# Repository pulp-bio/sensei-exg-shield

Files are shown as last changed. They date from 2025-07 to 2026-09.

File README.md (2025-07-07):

# SENSEI ExG shield

This repository contains the hardware design files for the **SENSEI ExG shield**, a versatile biopotential sensing shield for biopotential monitoring.

## Overview

The **SENSEI ExG Shield** provides a modular and configurable approach to biopotential measurements. It supports both balanced and unbalanced supply voltage configurations through different soldering options.

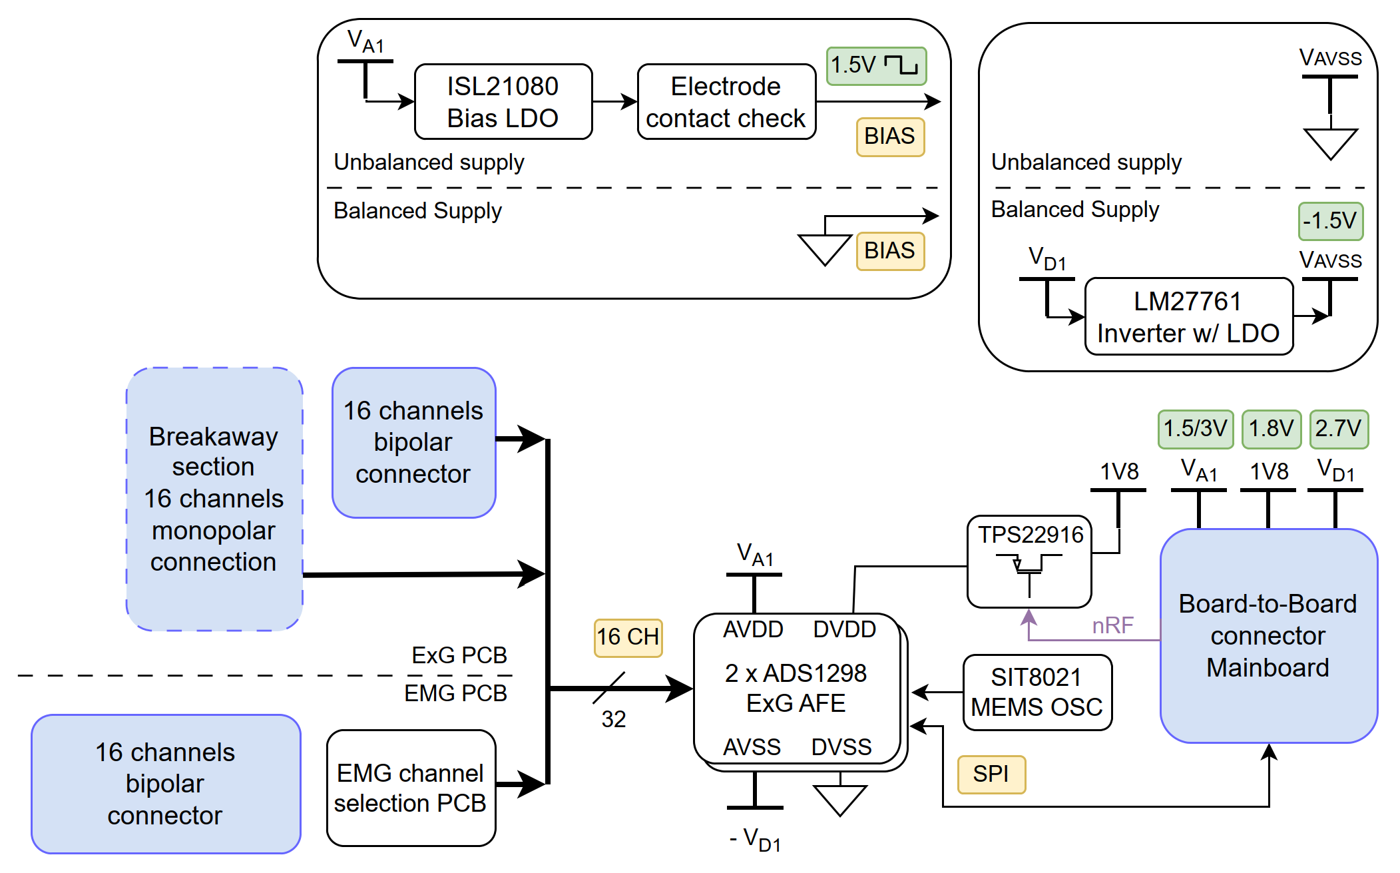
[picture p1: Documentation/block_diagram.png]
Block Diagram


### Key Features
- **16 biopotential channels**
- Supports both active and passive electrodes
- Configurable for fully differential and common-reference electrode setups
- Flexible supply voltage configuration (balanced and unbalanced)
- Stable MEMS-based clock (±50 ppm accuracy)

## Changelog
A changelog is available in the [Changelog.md](Changelog.md) file, which tracks all major updates and revisions to the board's design and documentation.

## Contributors
- **Sebastian Frey** ([sefrey@iis.ee.ethz.ch](mailto:sefrey@iis.ee.ethz.ch))

## License
This repository makes use of the following licenses:
- for all *hardware*: Solderpad Hardware License Version 0.51
- for all *images*: Creative Commons Attribution 4.0 International
License][cc-by]

For further information have a look at the license files: `LICENSE.hw`, `LICENSE.images`

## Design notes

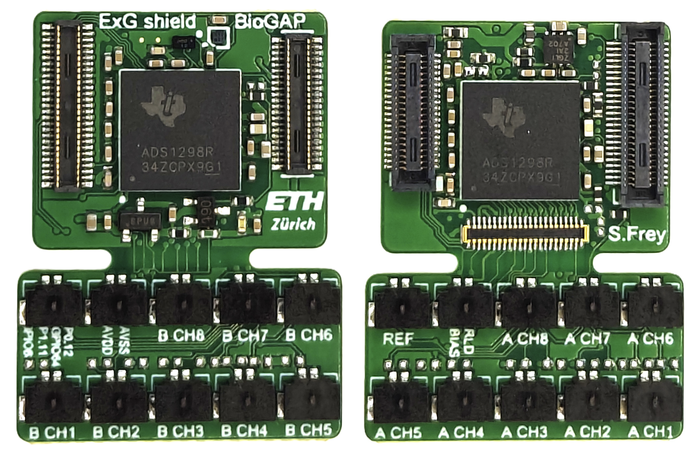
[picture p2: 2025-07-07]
Documentation/image_pcb.png

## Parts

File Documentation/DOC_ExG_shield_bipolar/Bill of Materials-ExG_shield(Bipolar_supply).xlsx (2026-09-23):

Comment | Description | Designator | Footprint | LibRef | Quantity
CL05A104KA5NNNC | Cap Ceramic 100nF 25V X5R ±10% SMD 0402 +85°C Paper T/R | C1, C3, C4, C7, C10, C15, C17, C18, C22, C25, C32, C33, C34, C40, C41, C43 | FP-CL278-IPC_C | CMP-13271-000728-1 | 16
CL05A105KP5NNNC | Cap Ceramic 1uF 10V X5R ±10% SMD 0402 +85°C Paper T/R | C2, C5, C6, C9, C11, C12, C16, C19, C20, C24, C26, C27, C37, C39, C42 | FP-CL511-IPC_C | CMP-13271-001936-1 | 15
CL05A106MP8NUB8 | Cap Ceramic 10uF 10V X5R ±20% SMD 0402 +85°C Paper T/R | C8, C23, C31 | FP-CL07-IPC_C | CMP-13271-002778-1 | 3
04025C102KAT2A | General Purpose Ceramic Capacitor, 0402, 1nF, 10%, X7R, 15%, 50V | C13, C28 | FP-0402-L_1_0_1-W_0_5_0_1-IPC_B | CMP-2008-02699-2 | 2
CL05A226MQ5QUNC | Cap Ceramic 22uF 6.3V X5R ±20% SMD 0402 +85°C Paper T/R | C14, C29 | FP-CL746-IPC_C | CMP-13271-000286-1 | 2
GRM155R71H152KA01D |  | C21 | CAPC1005X55X25NL05T10 | CMP-2008-04642-1 | 1
CGA2B3X7R1V103K050BB | Cap Ceramic 10nF 35V X7R 10% Pad SMD 0402 +125°C Automotive T/R | C30 | FP-CGA2B-MFG | CMP-08246-000497-1 | 1
GRM155Z71A225KE01D | Chip Multilayer Ceramic Capacitors for General Purpose, 0402, 2.2uF, X7R, 15%, 10%, 10V | C35 | FP-GRM155-0_15-IPC_B | CMP-06035-048202-1 | 1
CL05A475MP5NRNC | Cap Ceramic 4.7uF 10V X5R ±20% SMD 0402 +85°C Paper T/R | C36, C38 | FP-CL282-IPC_C | CMP-13271-000548-1 | 2
DF52-2S-0.8H_21_ | Connector | J1, J2, J7, J8, J9, J10, J11, J12, J13, J14, J15, J16, J17, J18, J19, J20, J21, J22, J23, J25 | DF522S08H21 | DF52-2S-0.8H_21_ | 20
DF40HC(2.5)-40DS-0.4V(51) | 40 Position 0.4mm Pitch Dual Row Vertical Surface Mount (SMT) Pin Socket, 2.5mm Stacking Height | J3 | DF40HC3040DS04V51 | DF40HC(3.0)-40DS-0.4V(51) | 1
DF40HC(2.5)-50DS-0.4V(51) | 50 Position 0.4mm Pitch Dual Row Vertical Surface Mount (SMT) Pin Socket, 2.5mm Stacking Height | J4 | DF40HC3050DS04V51 | DF40HC(3.0)-50DS-0.4V(51) | 1
DF40C-40DP-0.4V(51) | 50 Position 0.4mm Pitch Dual Row Vertical Surface Mount (SMT) Receptacle | J5 | FP-DF40C-40DP-0_4V_51-MFG | DF40C-40DP-0.4V(51) | 1
DF40C-50DP-0.4V(51) | 50 Position 0.4mm Pitch Dual Row Vertical Surface Mount (SMT) Receptacle, | J6 | CONN_COMBI_50P | DF40C-50DP-0.4V(51) | 1
505070-4222 | Connector | J24 | 5050704222 | 505070-4222 | 1
PMSS3906 | PNP Switching Transistor | Q1 | SOT323_N | PMSS3906 | 1
MCS04020C1004FE000 | RES SMD 1M OHM 1% 1/10W 0402 | R1 | FP-MCS0402-IPC_C | CMP-02407-000443-1 | 1
RT0402BRD0745K3L | RES 45.3K OHM 1/16W .1% SMD 0402 | R2 | FP-RT0402-MFG | CMP-03412-018483-1 | 1
RN73R1ETTP2003B25 | 200kΩ ±0.1% 0.063W, 1/16W Chip Resistor 0402 (1005 Metric) Moisture Resistant Thin Film | R3 | FP-RN73R1E-IPC_C | CMP-04015-050624-1 | 1
RC0402FR-070RL | RES SMD 0 OHM JUMPER 1/16W 0402 | R4, R13, R14 | FP-RC0402-0_4-IPC_A | CMP-2002-07342-2 | 3
RT0402FRE074K7L | RES 4.70K OHM 1/16W 1% SMD 0402 | R5 | FP-RT0402-MFG | CMP-2002-02901-2 | 1
TNPW040214K2BEED | RES 14.2K OHM 1/16W 1% SMD 0402 | R6 | FP-RT0402-MFG | CMP-2002-02901-2 | 1
RT0402BRD076K34L | RES 6.34K OHM 1/16W 1% SMD 0402 | R7 | FP-RT0402-MFG | CMP-2002-02901-2 | 1
RR0510P-563-D | 56kΩ ±0.5% 0.0625W 1/16W Chip Resistor 0402 (1005 Metric) Thin Film | R8 | FP-RR0510-MFG | CMP-2002-01632-2 | 1
RC0402FR-070RL | RES SMD 0 OHM JUMPER 1/16W 0402 | R10, R11, R12, R33 | FP-RC0402-0_4-IPC_C | CMP-2002-07342-2 | 4
ADS1298RIZXGT | 8-Channel, 24-Bit ADC with Integrated Respiration Impedance and ECG Front End, -40 to 85 degC, 64-pin BGA (ZXG64), Green (RoHS & no Sb/Br) | U1, U2 | TI-ZXG64 | CMP-0003-00996-1 | 2
ISL21080CIH320Z-TK | IC VREF SERIES 0.3% SOT23-3 | U3 | FP-P3_064A-IPC_C | CMP-13559-000004-1 | 1
LM27761DSGT | IC REG CHARGE PUMP ADJ 8WSON | U4 | FP-DSG0008A-MFG | CMP-04918-000089-1 | 1
SN74AUP2G125YZPR | Low-Power Dual Bus Buffer Gate With 3-State Outputs, YZP0008ADAD, LARGE T&R | U5 | YZP0008ADAD | CMP-0859-01143-3 | 1
TPS22916CYFPR | Integrated Circuit | U6 | BGA4C40P2X2_78X78X50 | TPS22916CYFPR | 1
SIT8021AC-J3-18S-2.048000 | MEMS OSC 2.048MHZ LVCMOS | Y1 | FP-SiT8021-MFG | CMP-25159-259502-1 | 1

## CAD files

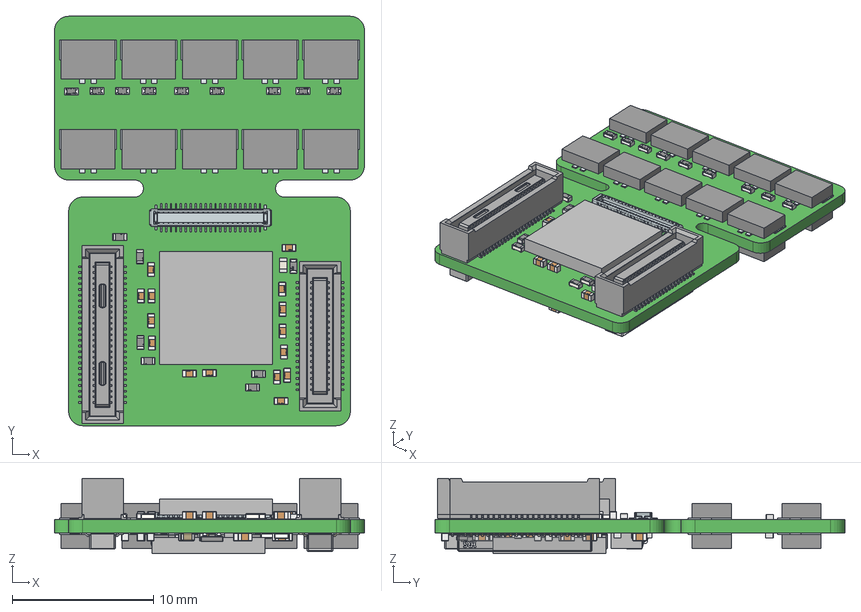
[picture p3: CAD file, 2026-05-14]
Documentation/ExG_shield_3D_step.step
21.9 x 29.0 x 5.32 mm
Pins x 20
logo x 56
pins x 20
terminals x 36
Yageo Logo x 7
Extruded x 6
Balls
0.1mm
Si Time Logo
IC_BODY
IC_LEG x 3
Renesas Logo
circle
Susumu Logo adjustable
top
TDK Logo
DF40C-50DP_RGB8421504
Hirose Electric
DF40HC(3.0)-40DS-0.4V
DF40HC(3.0)-50DS

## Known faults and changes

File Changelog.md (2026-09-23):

# Changelog

## [1.0.2] (23.09.2026)

### Added

- SPI clk of ADS A and ADS B are now disconnected when their respective CS is not low. This is done with MUX U5 (SN74AUP2G125YZPR).

### Fixed

- Unintended clear of the data ready signal of ADS A and B fixed by clk disconnection.

## [1.0.1] (14.05.2026)

### Added

### Changed

- Clock source of ADS1298 is fixed to external oscillator
- Pin from board-to-board connector nRF_P0.05 is not used anymore for clk source selection

## [1.0.0] (03.07.2025)
- Inital version

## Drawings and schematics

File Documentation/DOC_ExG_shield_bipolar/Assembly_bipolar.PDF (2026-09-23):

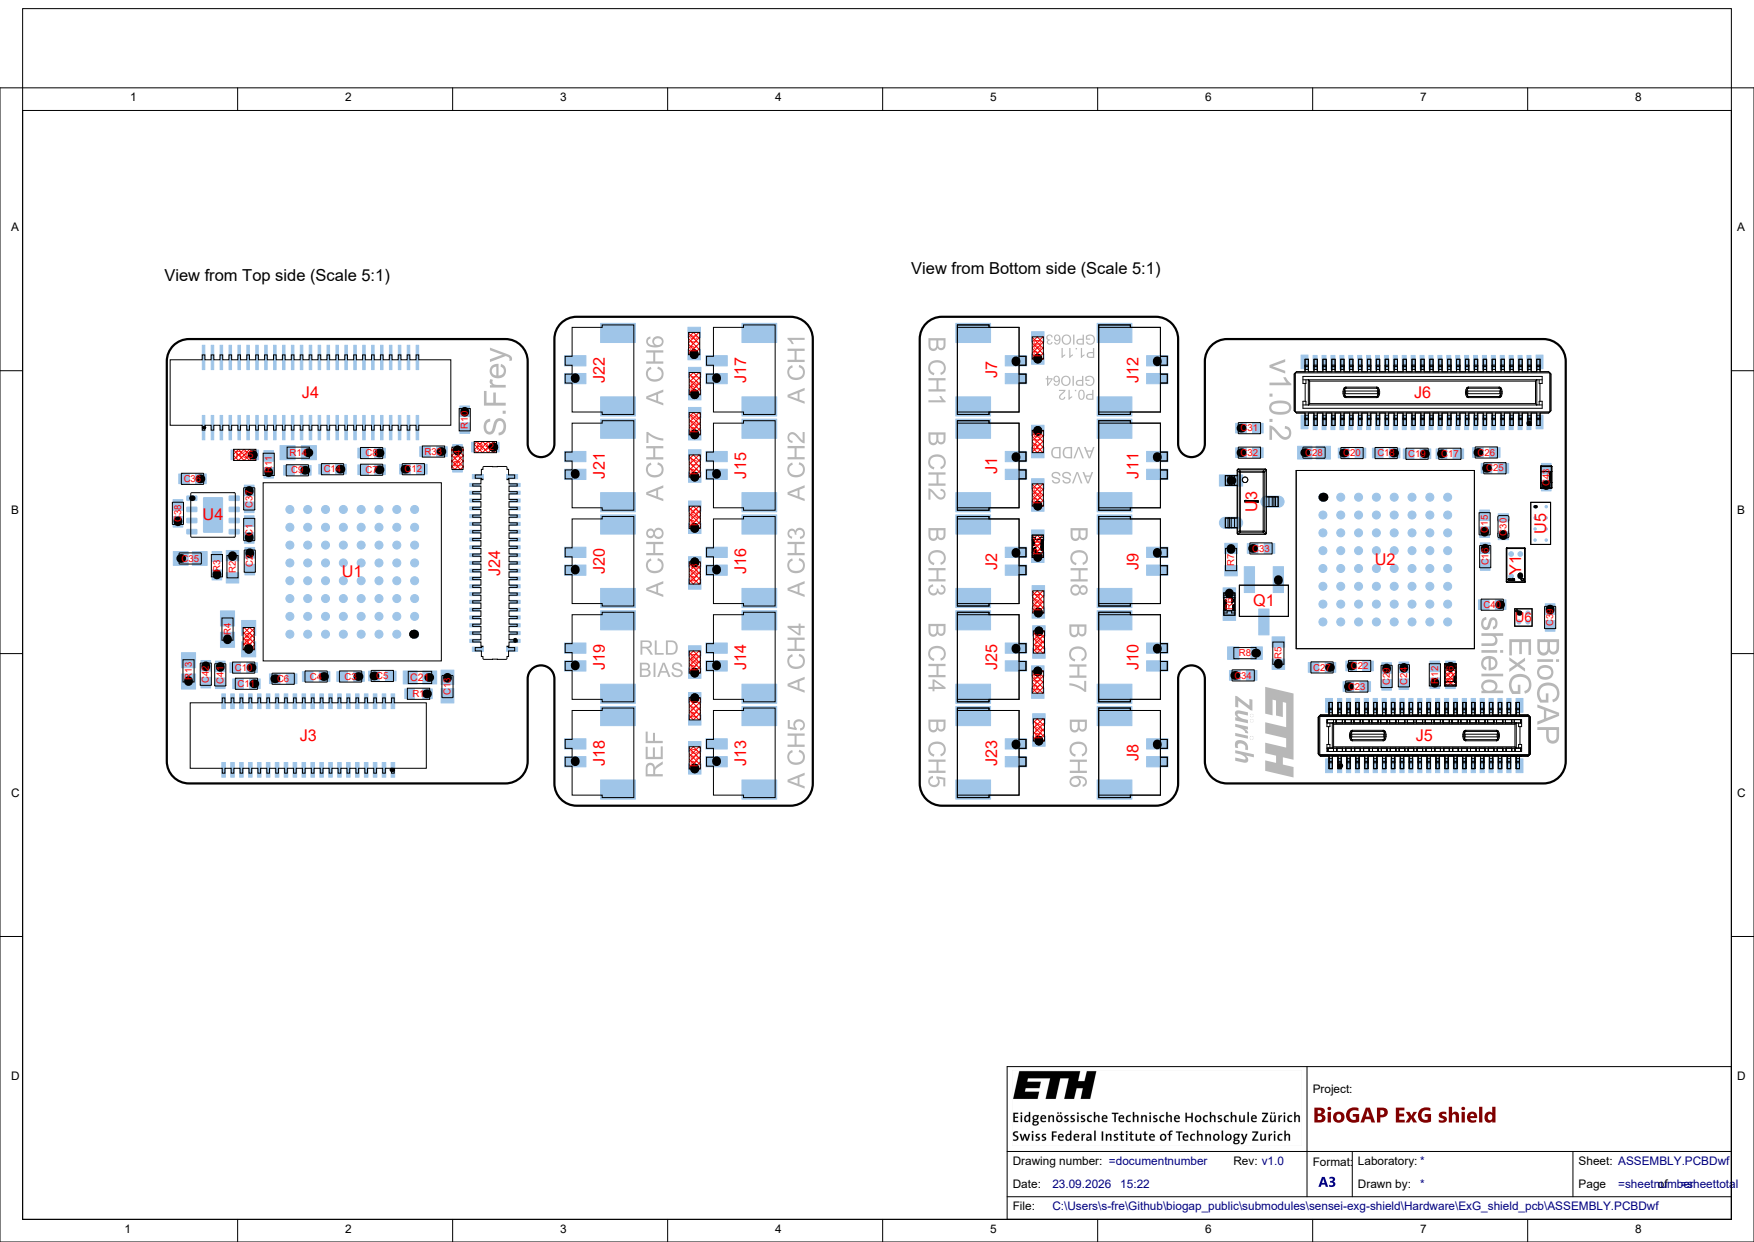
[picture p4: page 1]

View from Top side (Scale 5:1)

View from Bottom side (Scale 5:1)

Sheet:
Page =sheetnumber of =sheettotal

C:\Users\s-fre\Github\biogap_public\submodules\sensei-exg-shield\Hardware\ExG_shield_pcb\ASSEMBLY.PCBDwf

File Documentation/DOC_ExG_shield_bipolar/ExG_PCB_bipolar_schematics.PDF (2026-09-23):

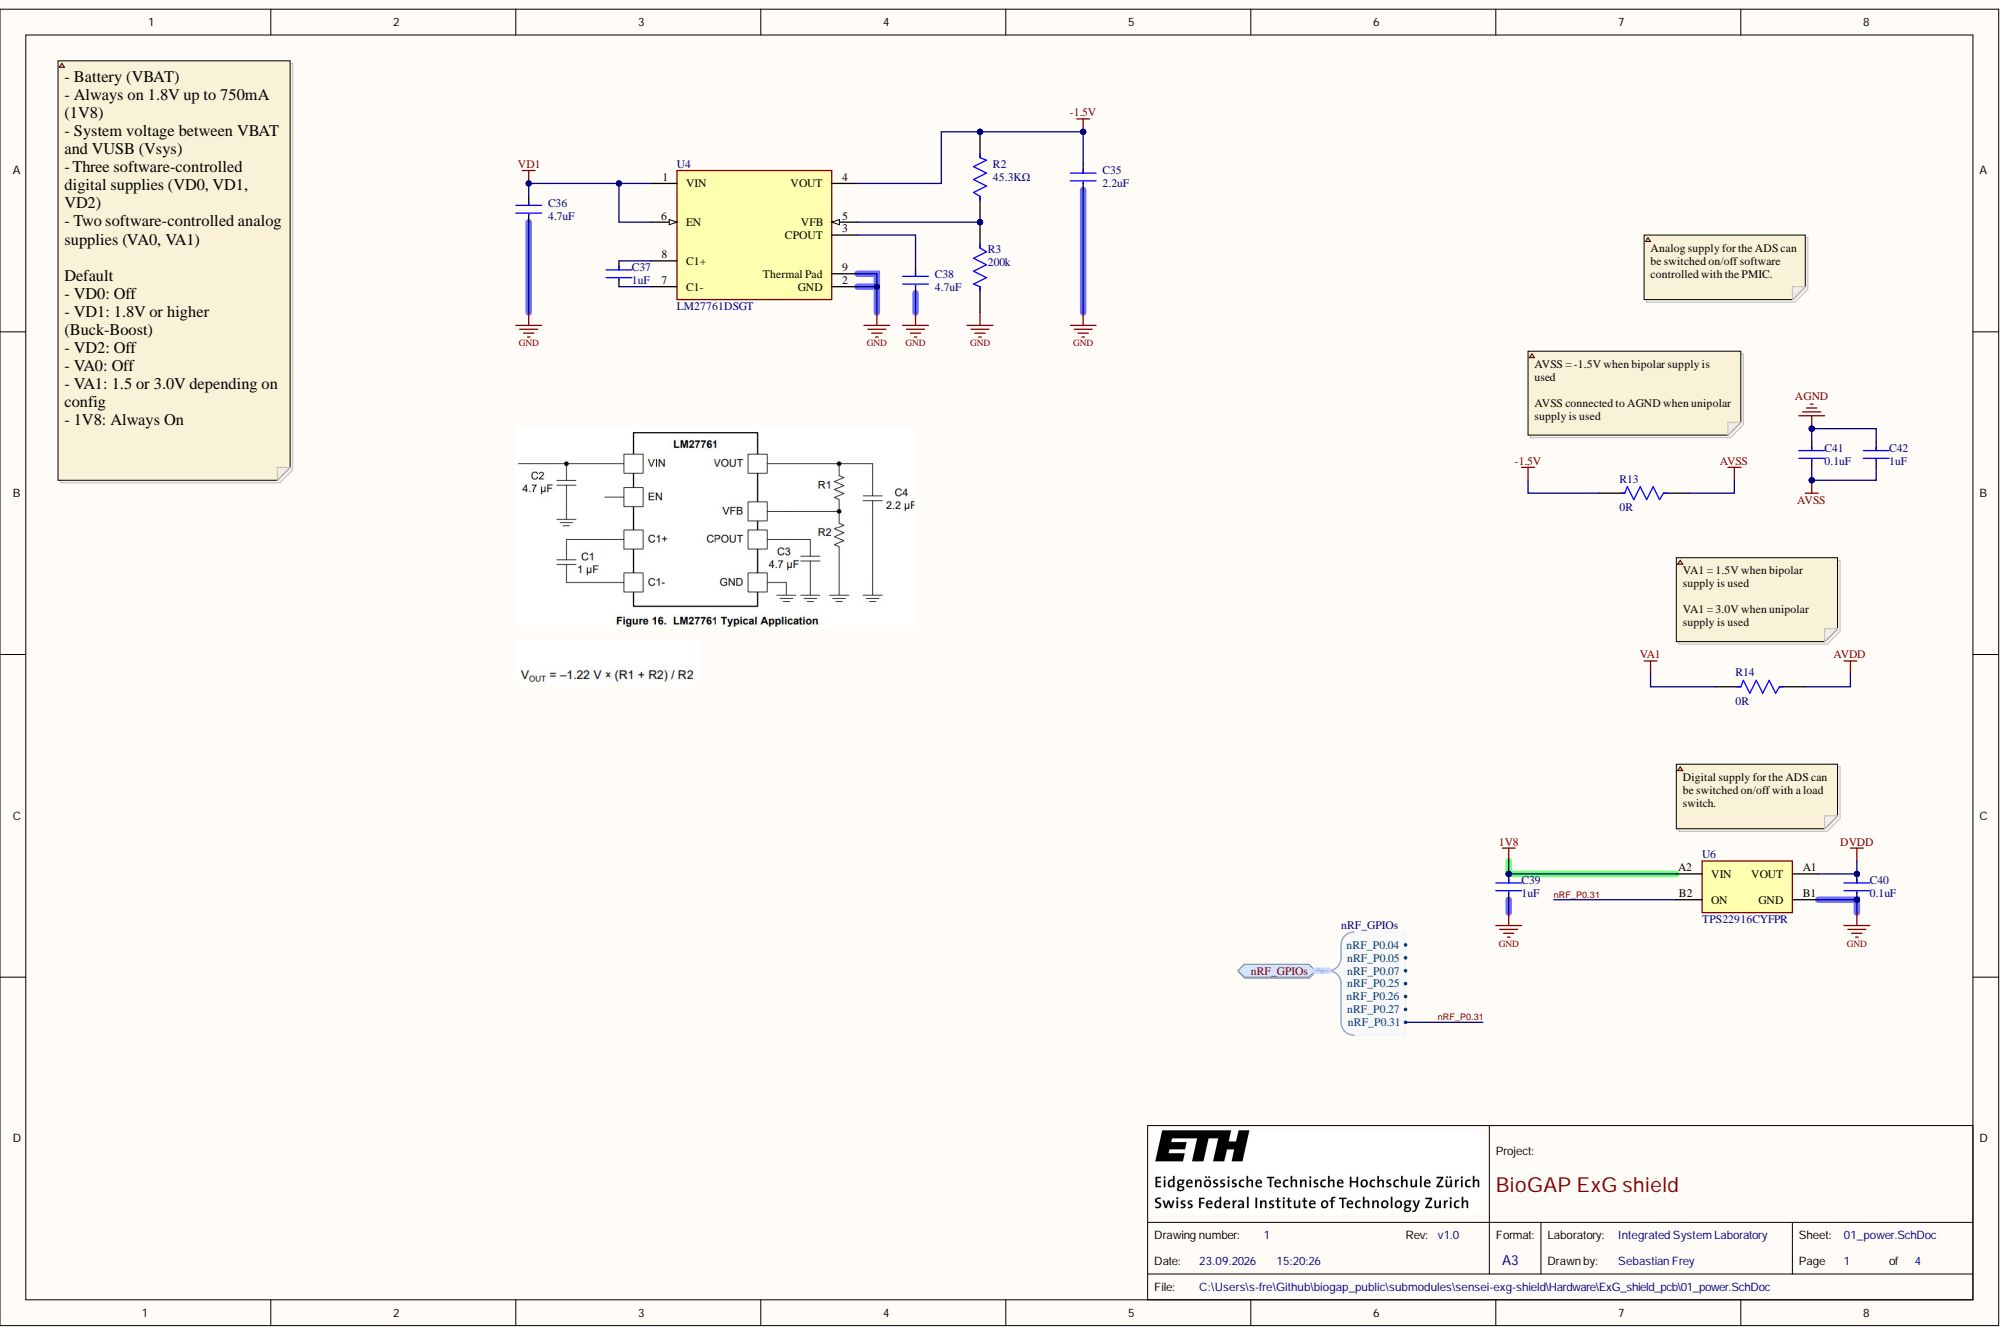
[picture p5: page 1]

- Battery (VBAT)
- Always on 1.8V up to 750mA
- System voltage between VBAT
and VUSB (Vsys)
- Three software-controlled
digital supplies (VD0, VD1,
- Two software-controlled analog
supplies (VA0, VA1)

Analog supply for the ADS can
be switched on/off software
controlled with the PMIC.

AVSS = -1.5V when bipolar supply is
used

AVSS connected to AGND when unipolar
supply is used

Digital supply for the ADS can
be switched on/off with a load
switch.

Project: BioGAP ExG shield

Drawing number: 1 Rev: v1.0 Date: 23.09.2026 15:20:26 | Format: A3 | Laboratory: Integrated System Laboratory Drawn by: Sebastian Frey | Sheet: 01_power.SchDoc Page 1 of 4

C:\Users\s-fre\Github\biogap_public\submodules\sensei-exg-shield\Hardware\ExG_shield_pcb\01_power.SchDoc

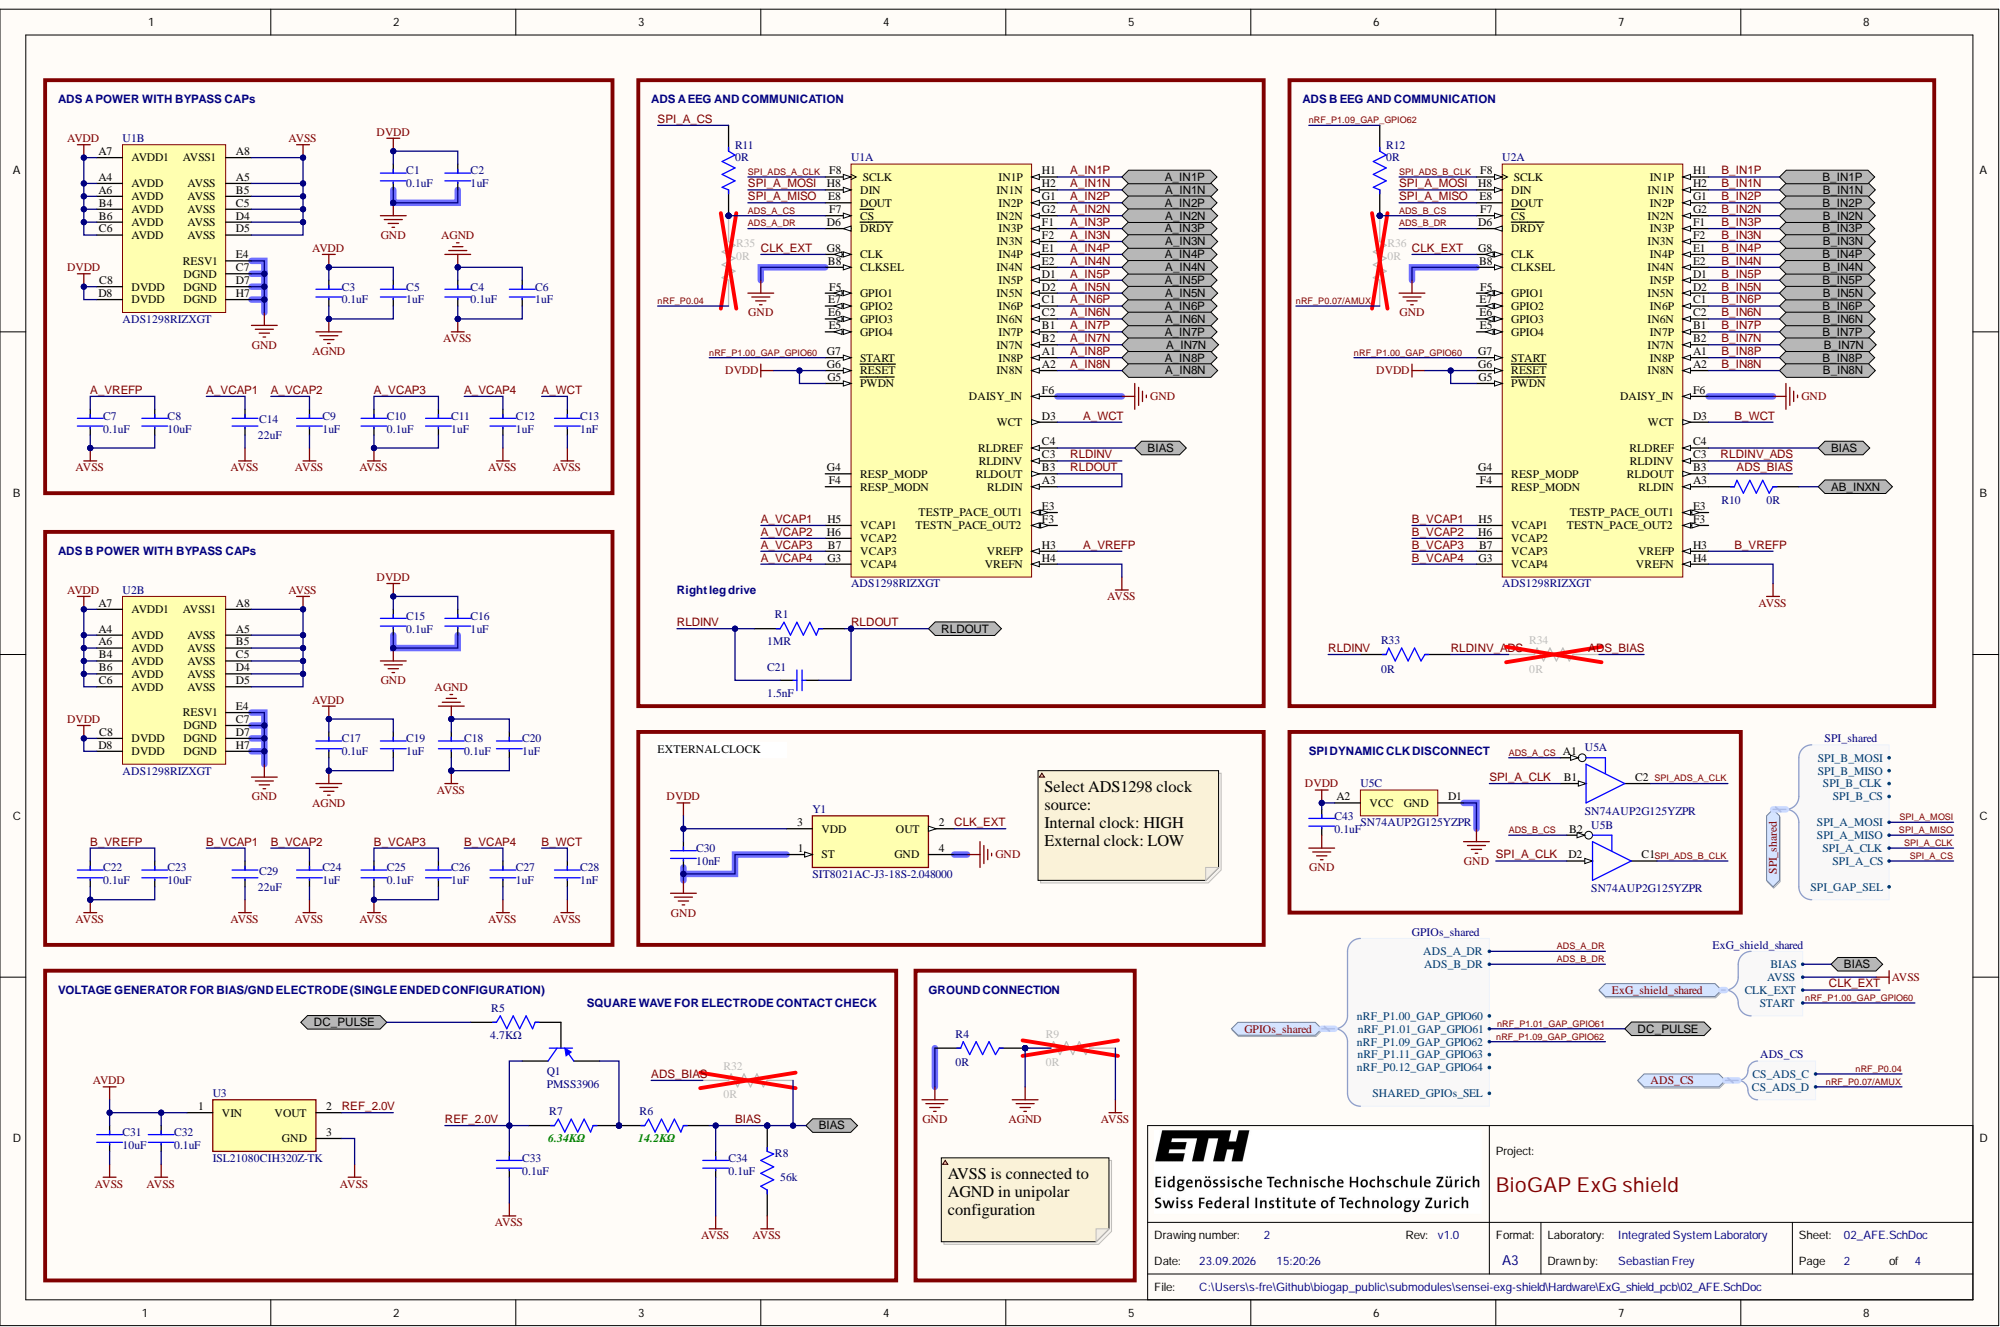
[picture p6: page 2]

ADS A POWER WITH BYPASS CAPs

ADS AEEG AND COMMUNICATION

ADS B EEG AND COMMUNICATION

ADS B POWER WITH BYPASS CAPs

SPI DYNAMIC CLK DISCONNECT

VOLTAGE GENERATOR FOR BIAS/GND ELECTRODE (SINGLE ENDED CONFIGURATION)

SQUARE WAVE FOR ELECTRODE CONTACT CHECK

AVSS is connected to
AGND in unipolar
configuration

C:\Users\s-fre\Github\biogap_public\submodules\sensei-exg-shield\Hardware\ExG_shield_pcb\02_AFE.SchDoc

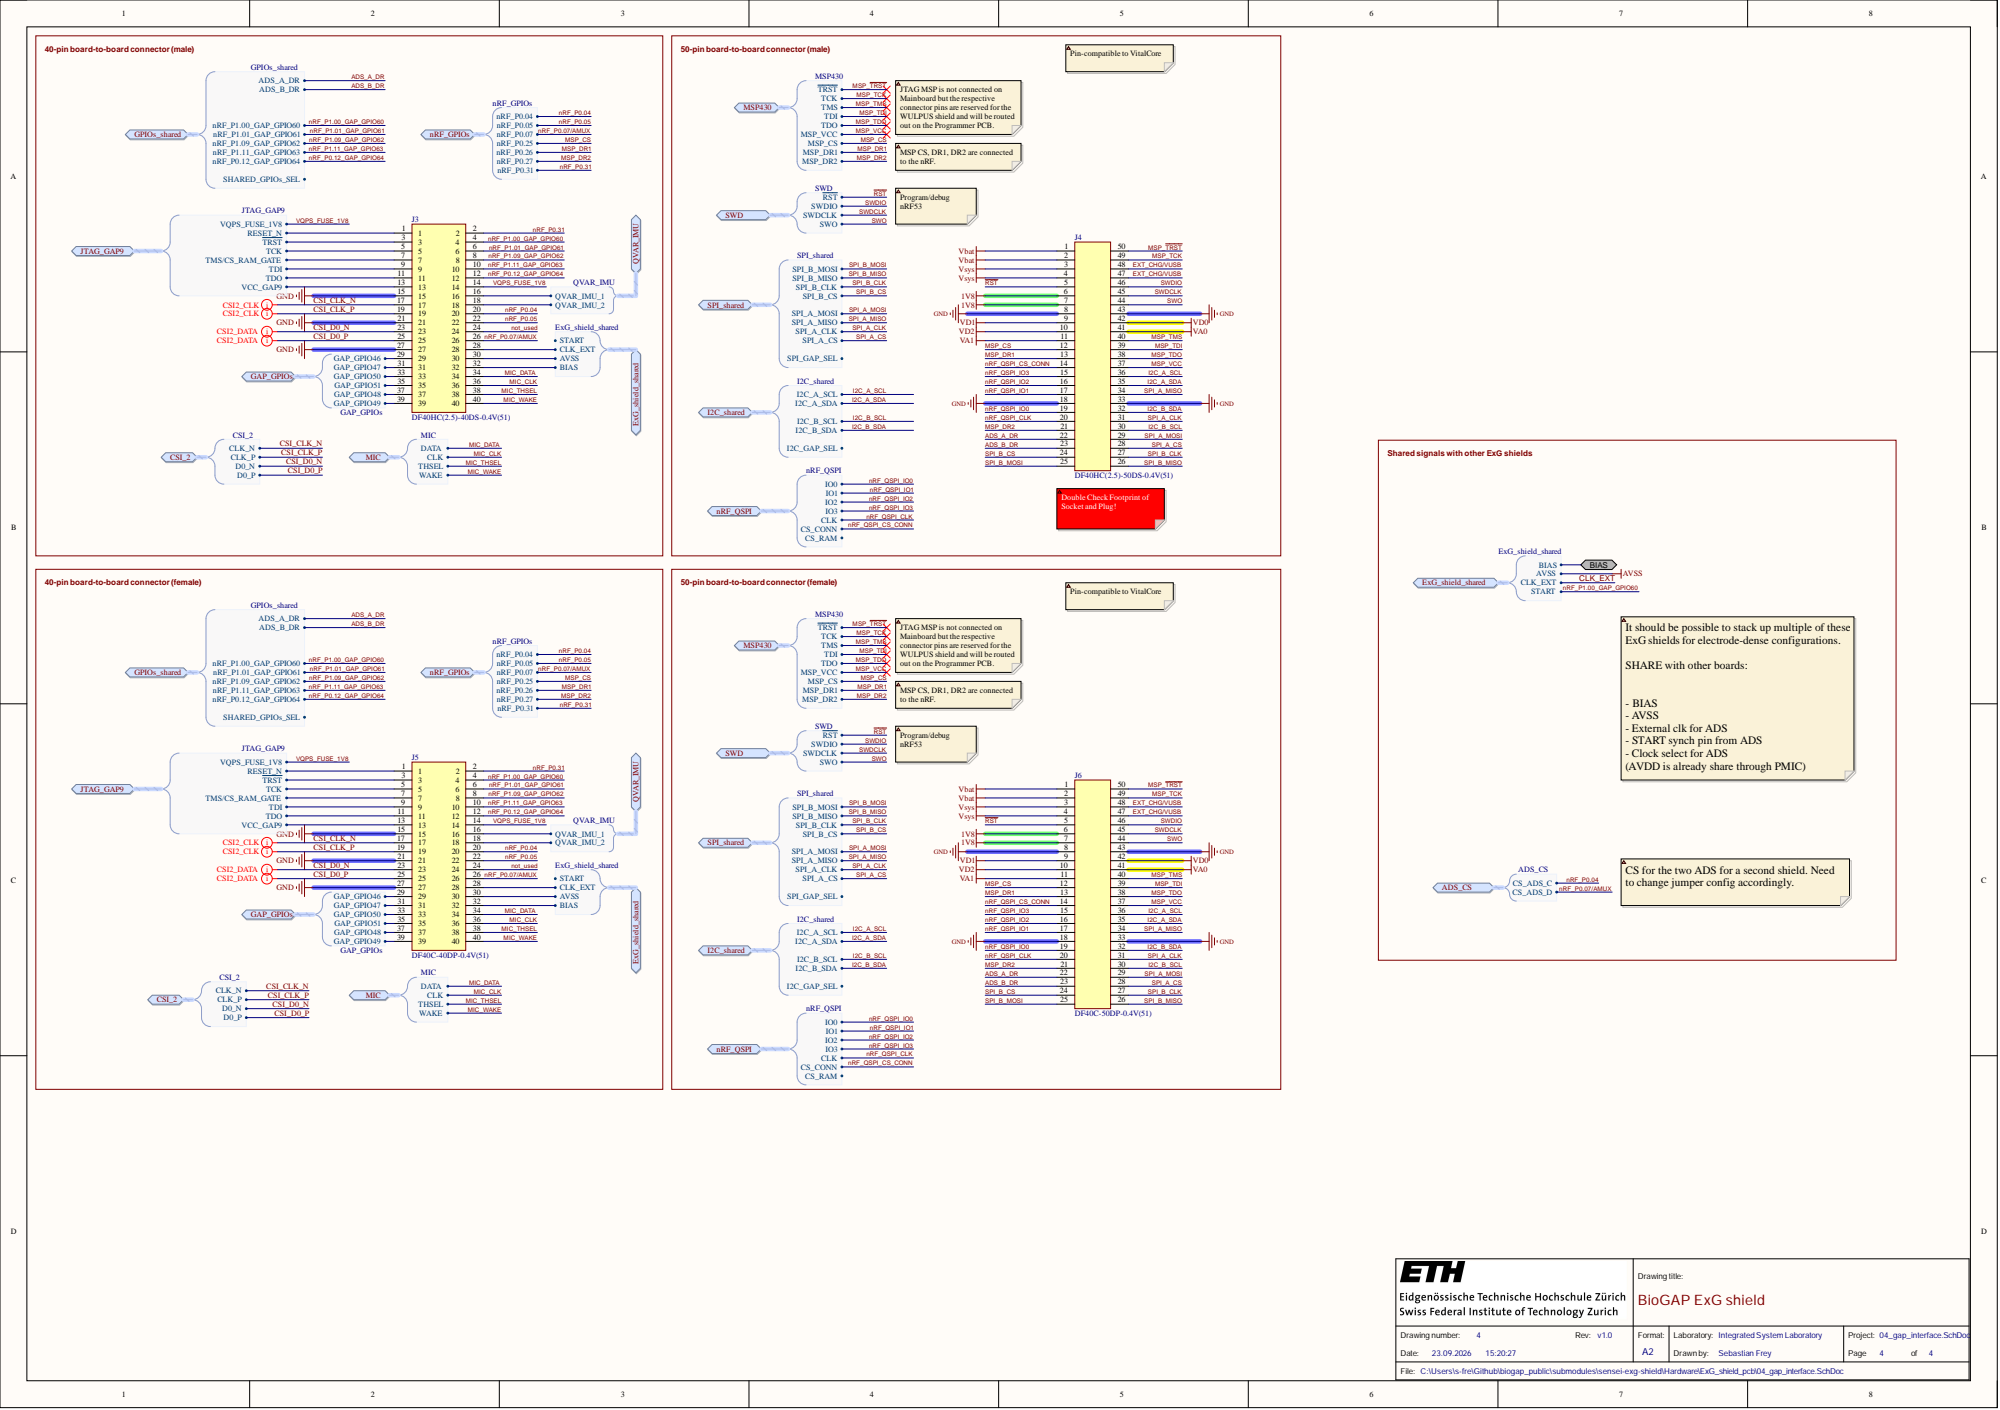
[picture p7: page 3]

40-pin board-to-board connector(male)

50-pin board-to-board connector(male)

Pin-compatible to VitalCore

JTAG MSP is not connected on
Mainboard but the respective
connector pins are reserved for the
WULPUS shield and will be routed
out on the Programmer PCB.

MSP CS, DR1, DR2 are connected
to the nRF.

Shared signals with other ExG shields

Double Check Footprint of
Socket and Plug!

It should be possible to stack up multiple of these
ExG shields for electrode-dense configurations.

SHARE with other boards:

- BIAS
- AVSS
- External clk for ADS
- START synch pin from ADS
- Clock select for ADS
(AVDD is already share through PMIC)

CS for the two ADS for a second shield. Need
to change jumper config accordingly.

Drawing title: BioGAP ExG shield

Project: 04_gap_interface.SchDoc Page 4 of 4

C:\Users\s-fre\Github\biogap_public\submodules\sensei-exg-shield\Hardware\ExG_shield_pcb\04_gap_interface.SchDoc

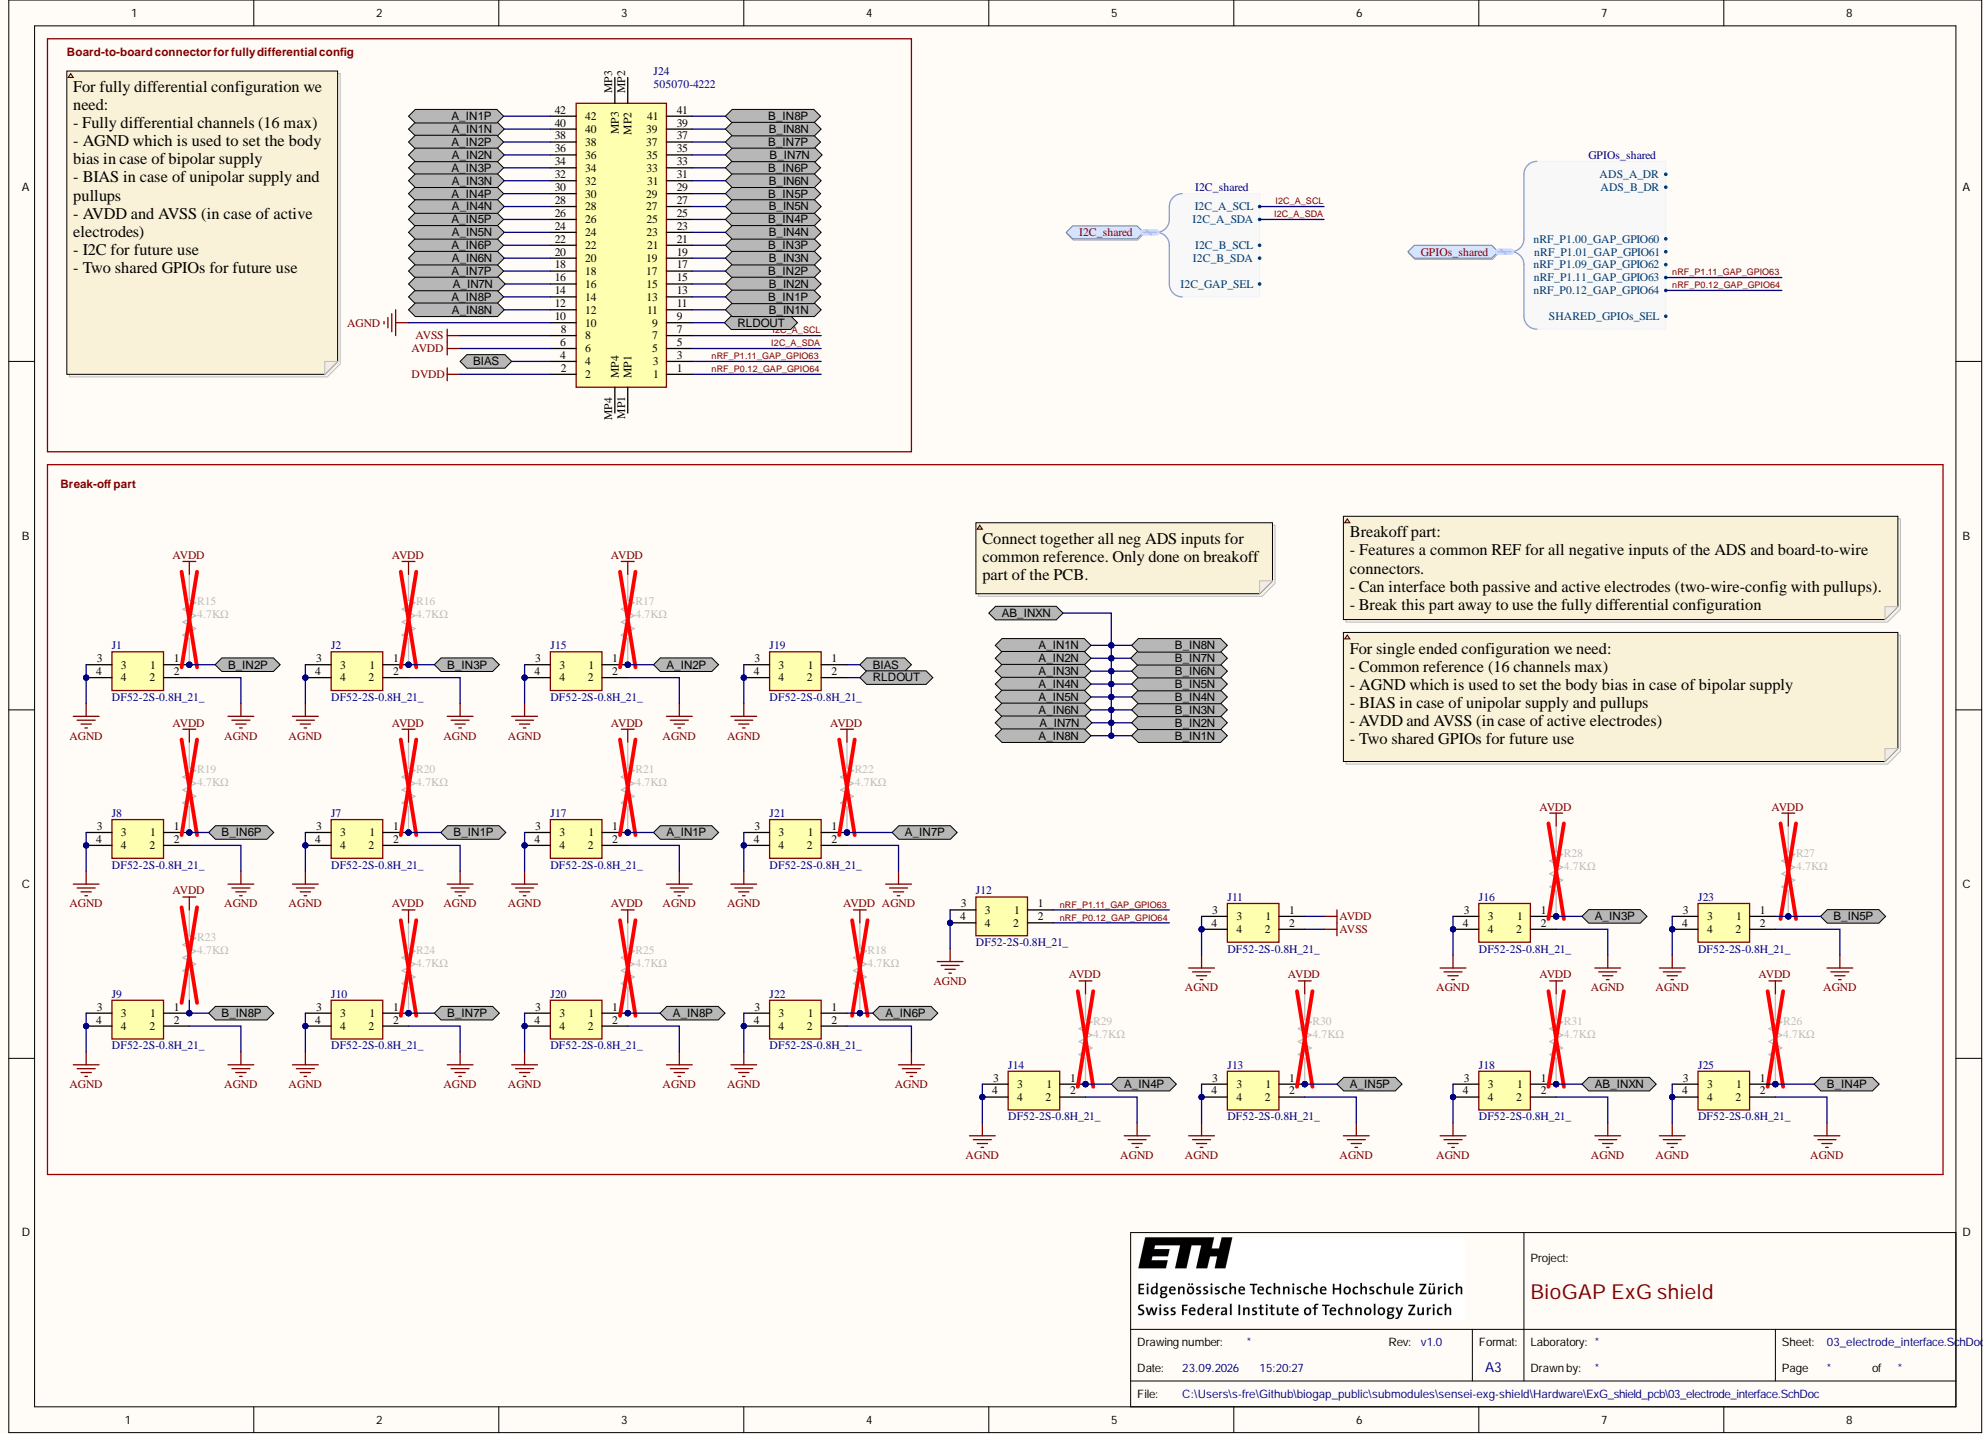
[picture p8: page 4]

Board-to-board connectorforfullydifferential config

For fully differential configuration we
need:
- Fully differential channels (16 max)
- AGND which is used to set the body
bias in case of bipolar supply
- BIAS in case of unipolar supply and
pullups
- AVDD and AVSS (in case of active
electrodes)
- I2C for future use
- Two shared GPIOs for future use

Connect together all neg ADS inputs for
common reference. Only done on breakoff
part of the PCB.

Breakoff part:
- Features a common REF for all negative inputs of the ADS and board-to-wire
connectors.
- Can interface both passive and active electrodes (two-wire-config with pullups).
- Break this part away to use the fully differential configuration

For single ended configuration we need:
- Common reference (16 channels max)
- AGND which is used to set the body bias in case of bipolar supply
- BIAS in case of unipolar supply and pullups
- AVDD and AVSS (in case of active electrodes)

Project: BioGAP ExG shield

Drawing number: * | | Laboratory: * * | Page * of *

C:\Users\s-fre\Github\biogap_public\submodules\sensei-exg-shield\Hardware\ExG_shield_pcb\03_electrode_interface.SchDoc

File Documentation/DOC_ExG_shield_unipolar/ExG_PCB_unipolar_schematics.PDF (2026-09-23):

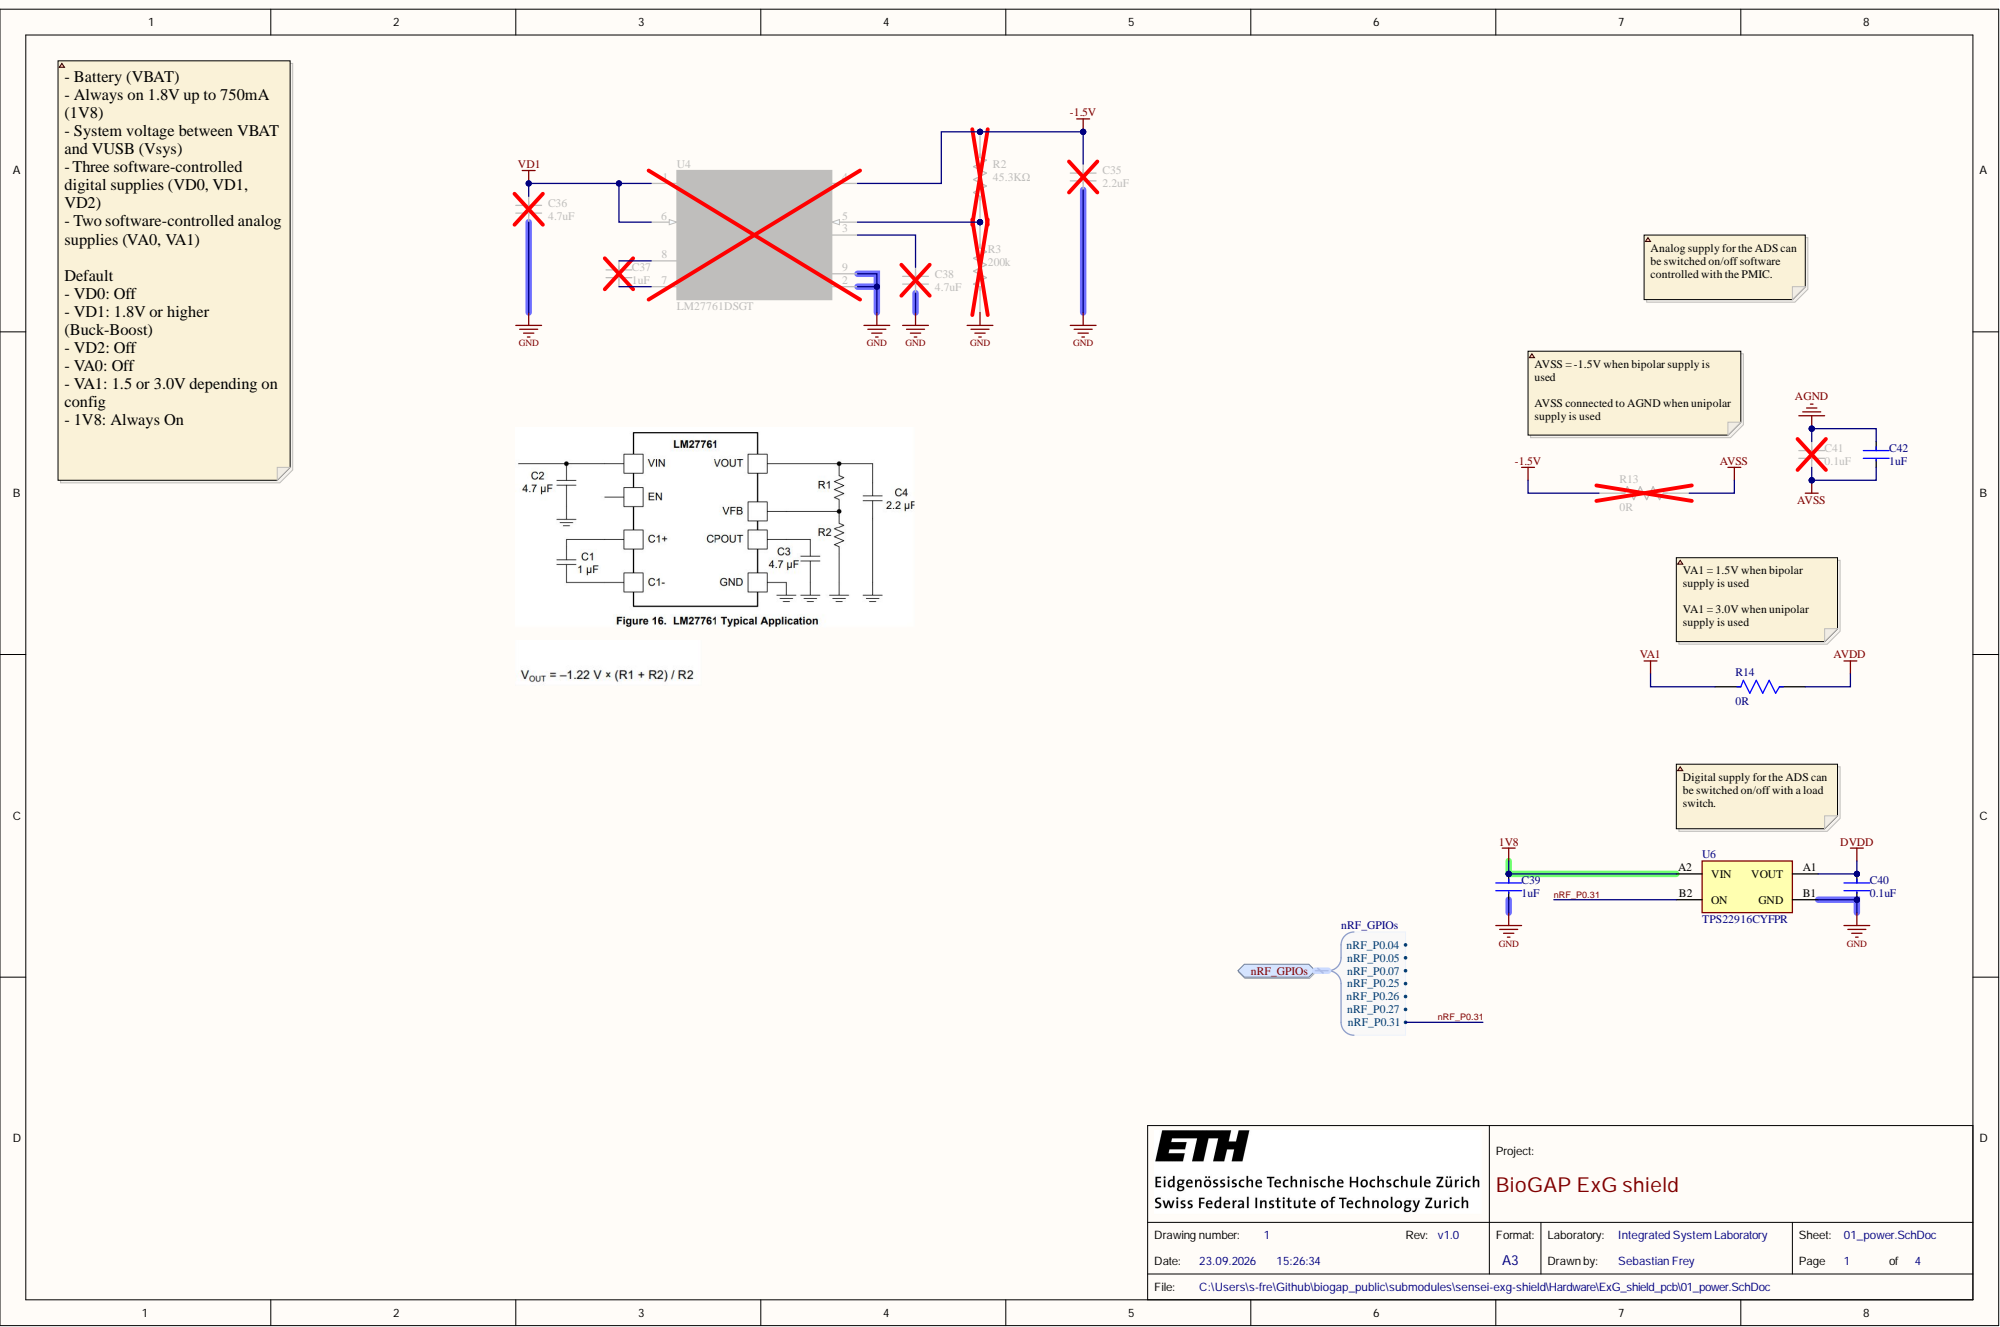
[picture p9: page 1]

- Battery (VBAT)
- Always on 1.8V up to 750mA
- System voltage between VBAT
and VUSB (Vsys)
- Three software-controlled
digital supplies (VD0, VD1,
- Two software-controlled analog
supplies (VA0, VA1)

Analog supply for the ADS can
be switched on/off software
controlled with the PMIC.

AVSS = -1.5V when bipolar supply is
used

AVSS connected to AGND when unipolar
supply is used

Digital supply for the ADS can
be switched on/off with a load
switch.

Project: BioGAP ExG shield

Drawing number: 1 Rev: v1.0 Date: 23.09.2026 15:26:34 | Format: A3 | Laboratory: Integrated System Laboratory Drawn by: Sebastian Frey | Sheet: 01_power.SchDoc Page 1 of 4

C:\Users\s-fre\Github\biogap_public\submodules\sensei-exg-shield\Hardware\ExG_shield_pcb\01_power.SchDoc

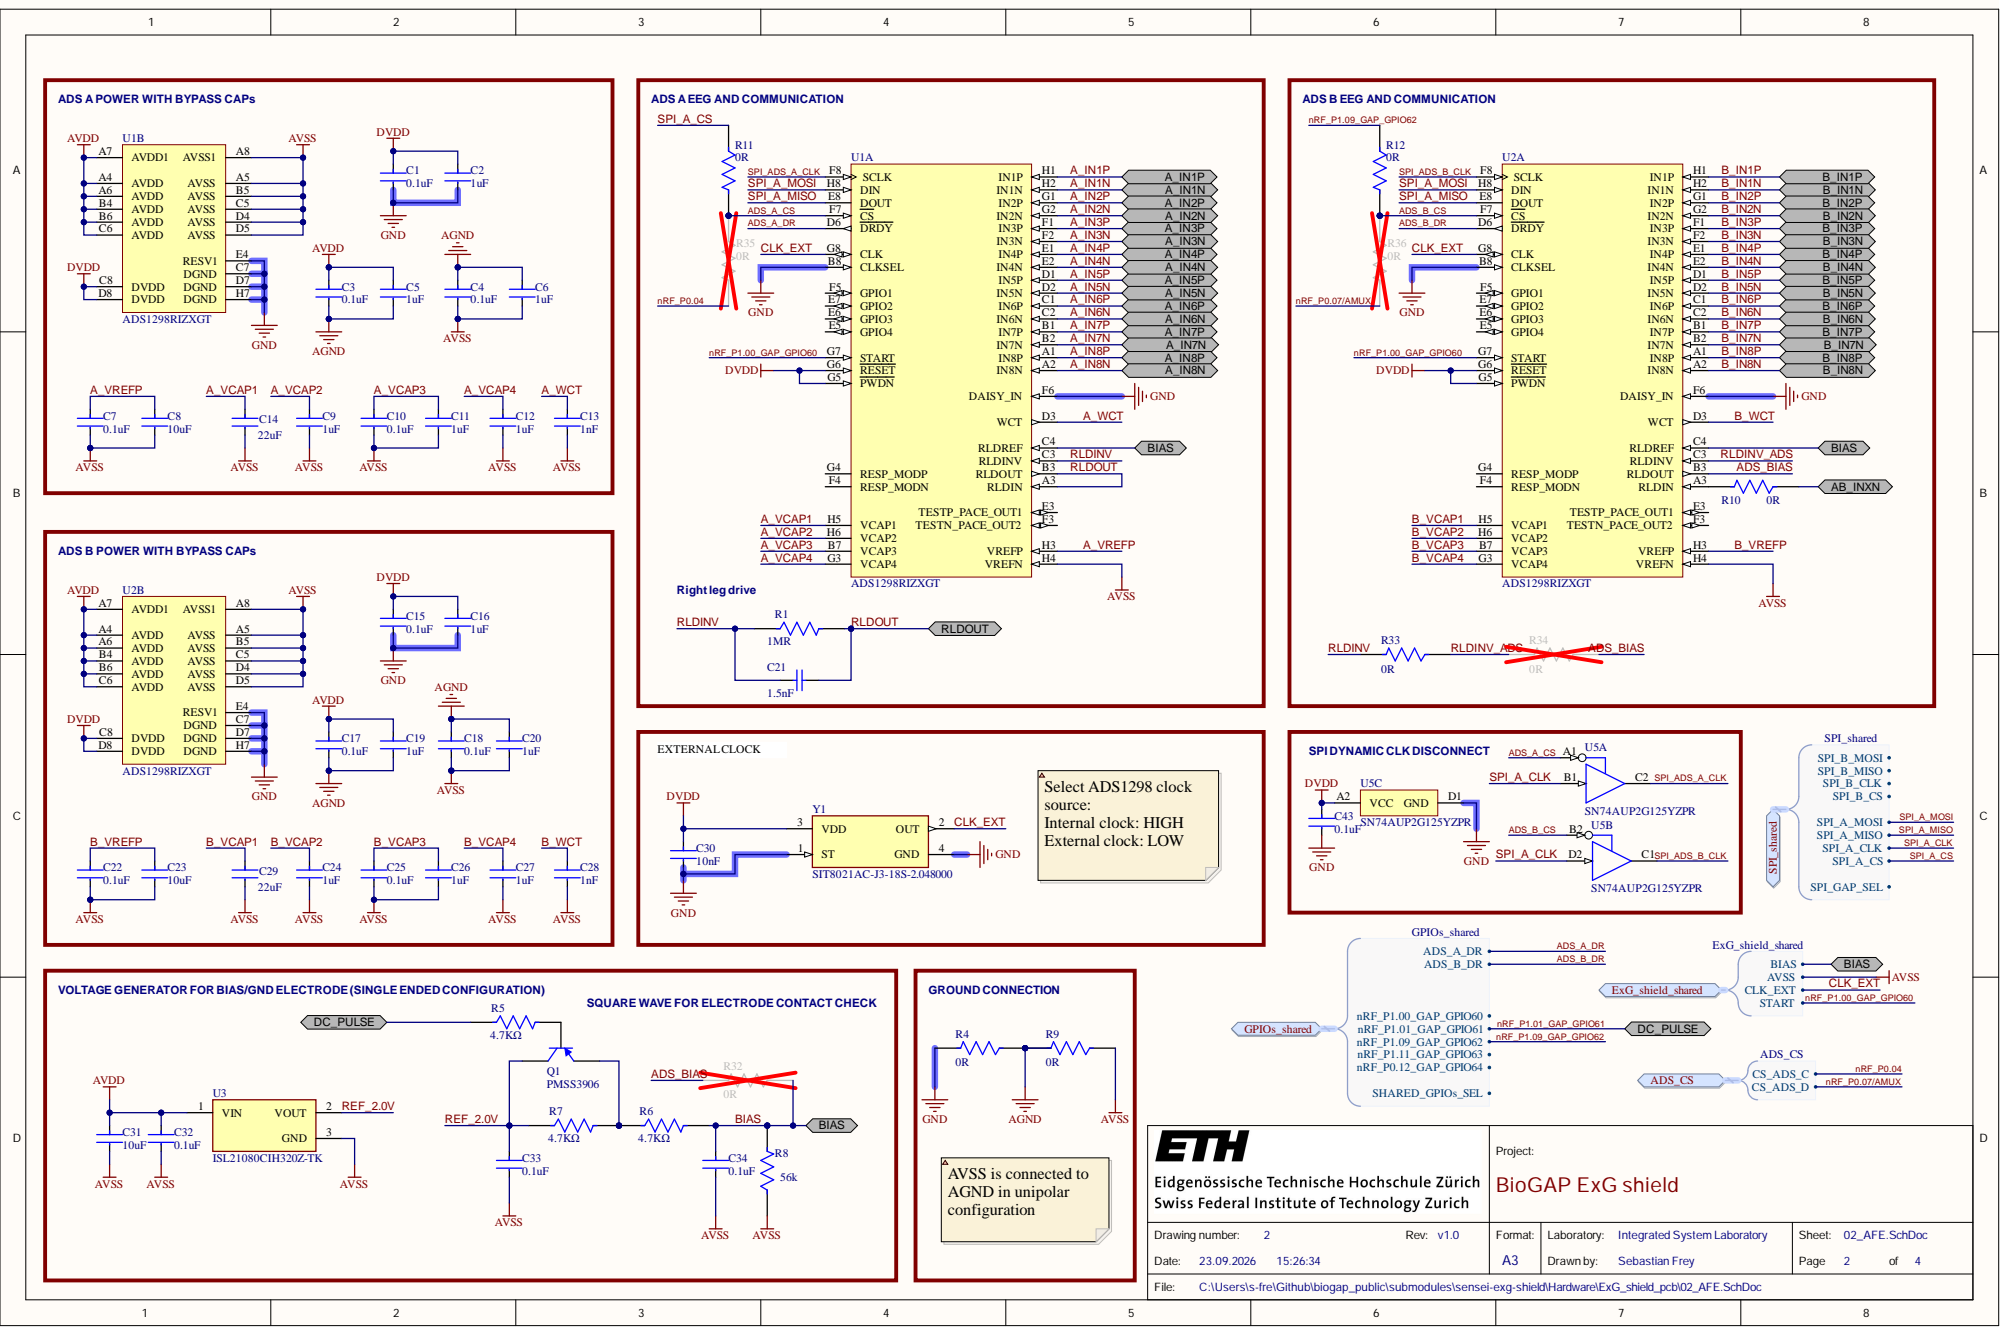
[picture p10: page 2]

ADS A POWER WITH BYPASS CAPs

ADS AEEG AND COMMUNICATION

ADS B EEG AND COMMUNICATION

ADS B POWER WITH BYPASS CAPs

SPI DYNAMIC CLK DISCONNECT

VOLTAGE GENERATOR FOR BIAS/GND ELECTRODE (SINGLE ENDED CONFIGURATION)

SQUARE WAVE FOR ELECTRODE CONTACT CHECK

AVSS is connected to
AGND in unipolar
configuration

C:\Users\s-fre\Github\biogap_public\submodules\sensei-exg-shield\Hardware\ExG_shield_pcb\02_AFE.SchDoc

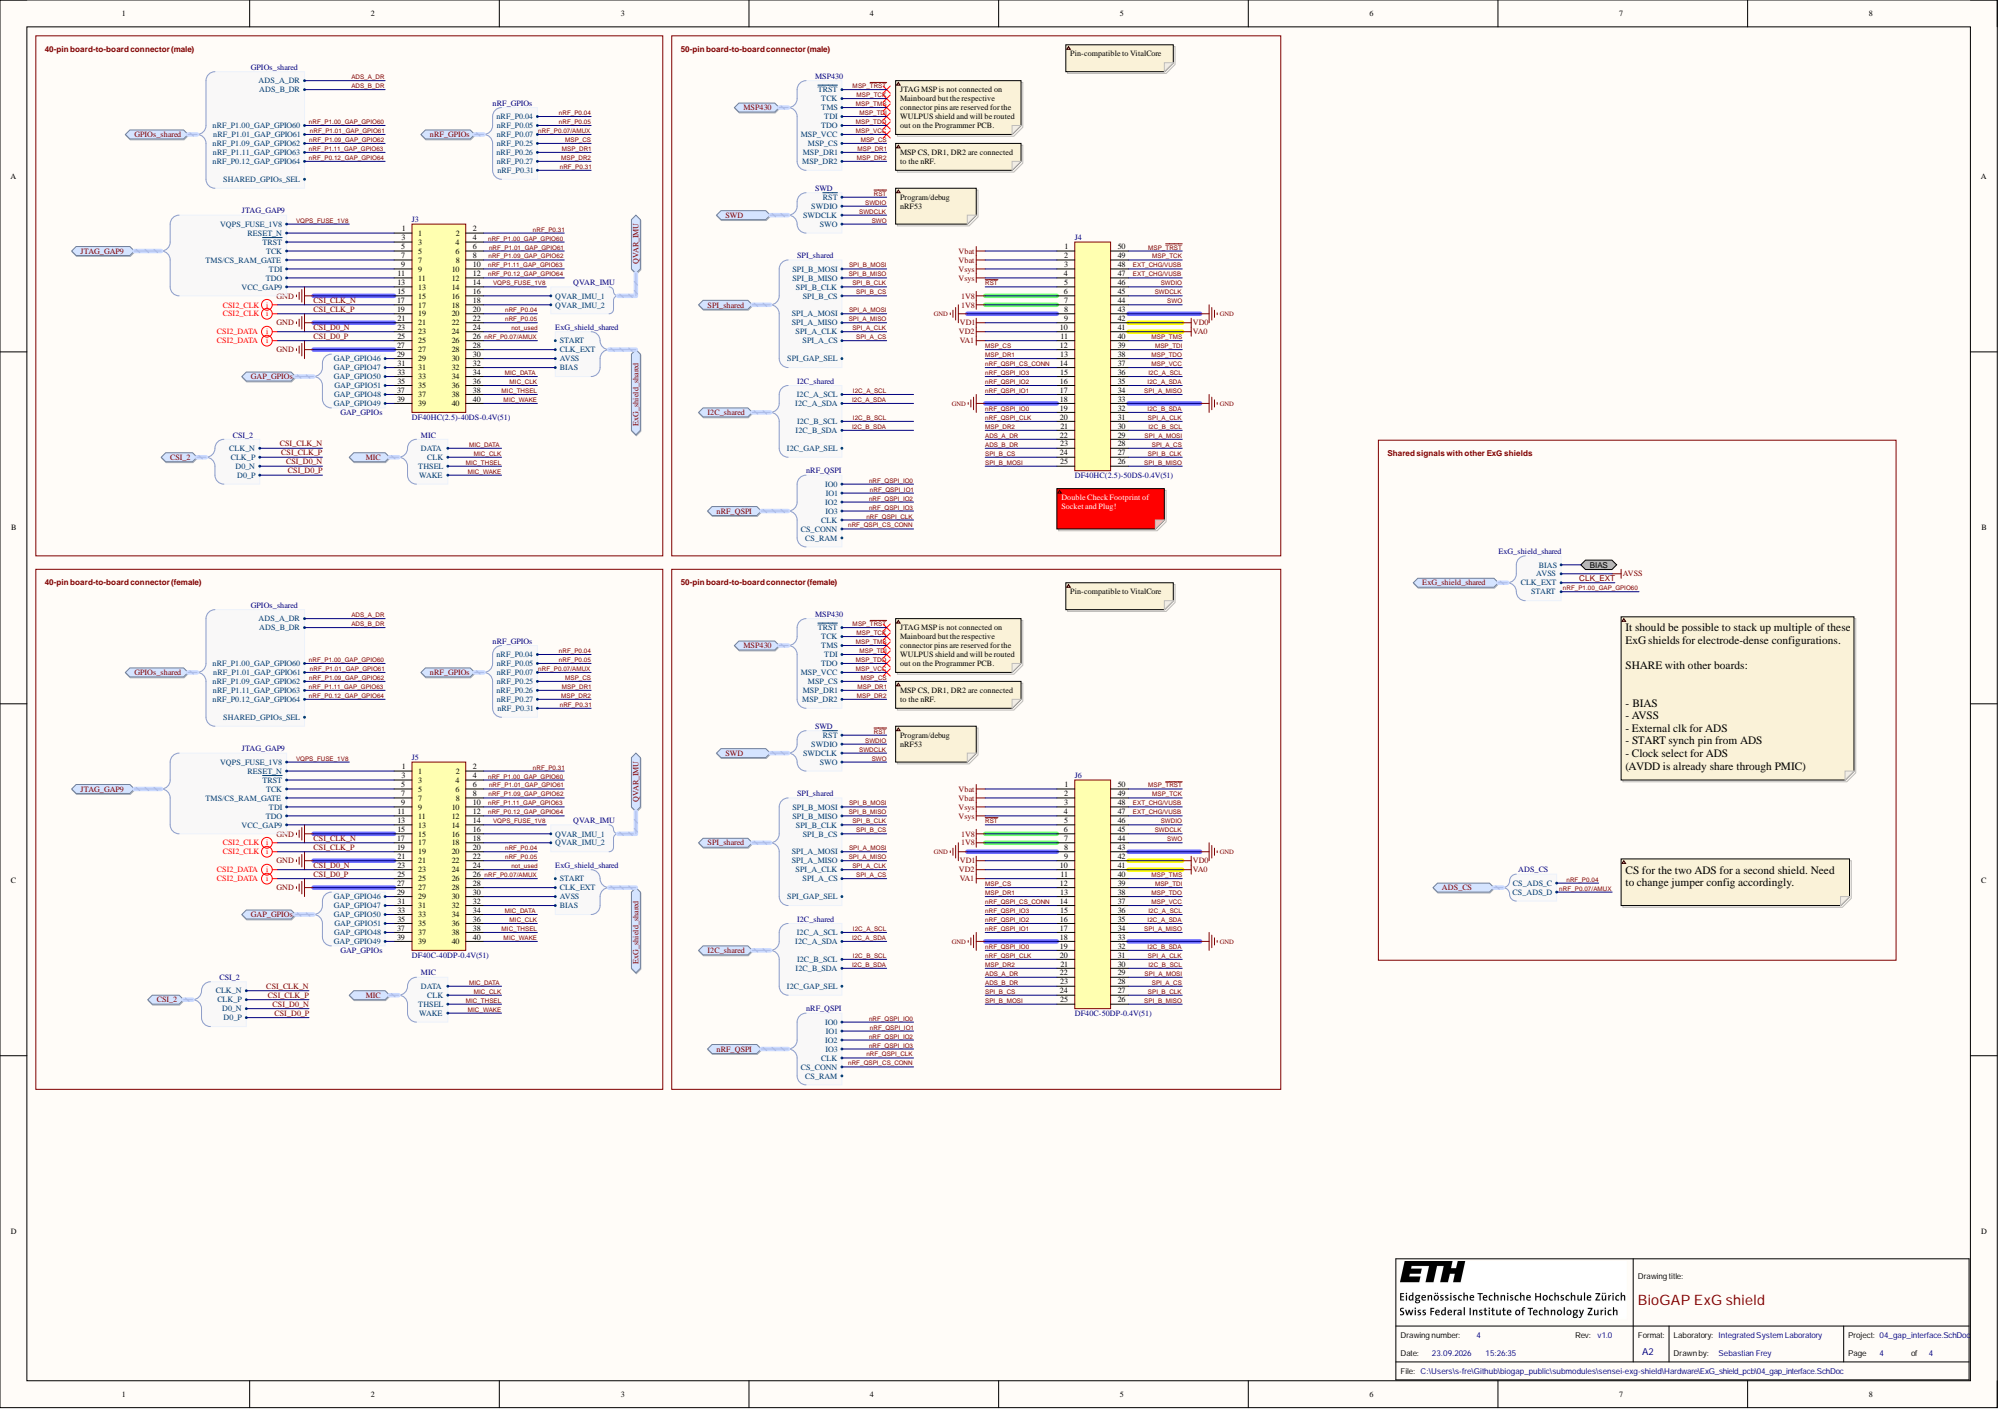
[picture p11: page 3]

40-pin board-to-board connector(male)

50-pin board-to-board connector(male)

Pin-compatible to VitalCore

JTAG MSP is not connected on
Mainboard but the respective
connector pins are reserved for the
WULPUS shield and will be routed
out on the Programmer PCB.

MSP CS, DR1, DR2 are connected
to the nRF.

Shared signals with other ExG shields

Double Check Footprint of
Socket and Plug!

It should be possible to stack up multiple of these
ExG shields for electrode-dense configurations.

SHARE with other boards:

- BIAS
- AVSS
- External clk for ADS
- START synch pin from ADS
- Clock select for ADS
(AVDD is already share through PMIC)

CS for the two ADS for a second shield. Need
to change jumper config accordingly.

Drawing title: BioGAP ExG shield

Project: 04_gap_interface.SchDoc Page 4 of 4

C:\Users\s-fre\Github\biogap_public\submodules\sensei-exg-shield\Hardware\ExG_shield_pcb\04_gap_interface.SchDoc

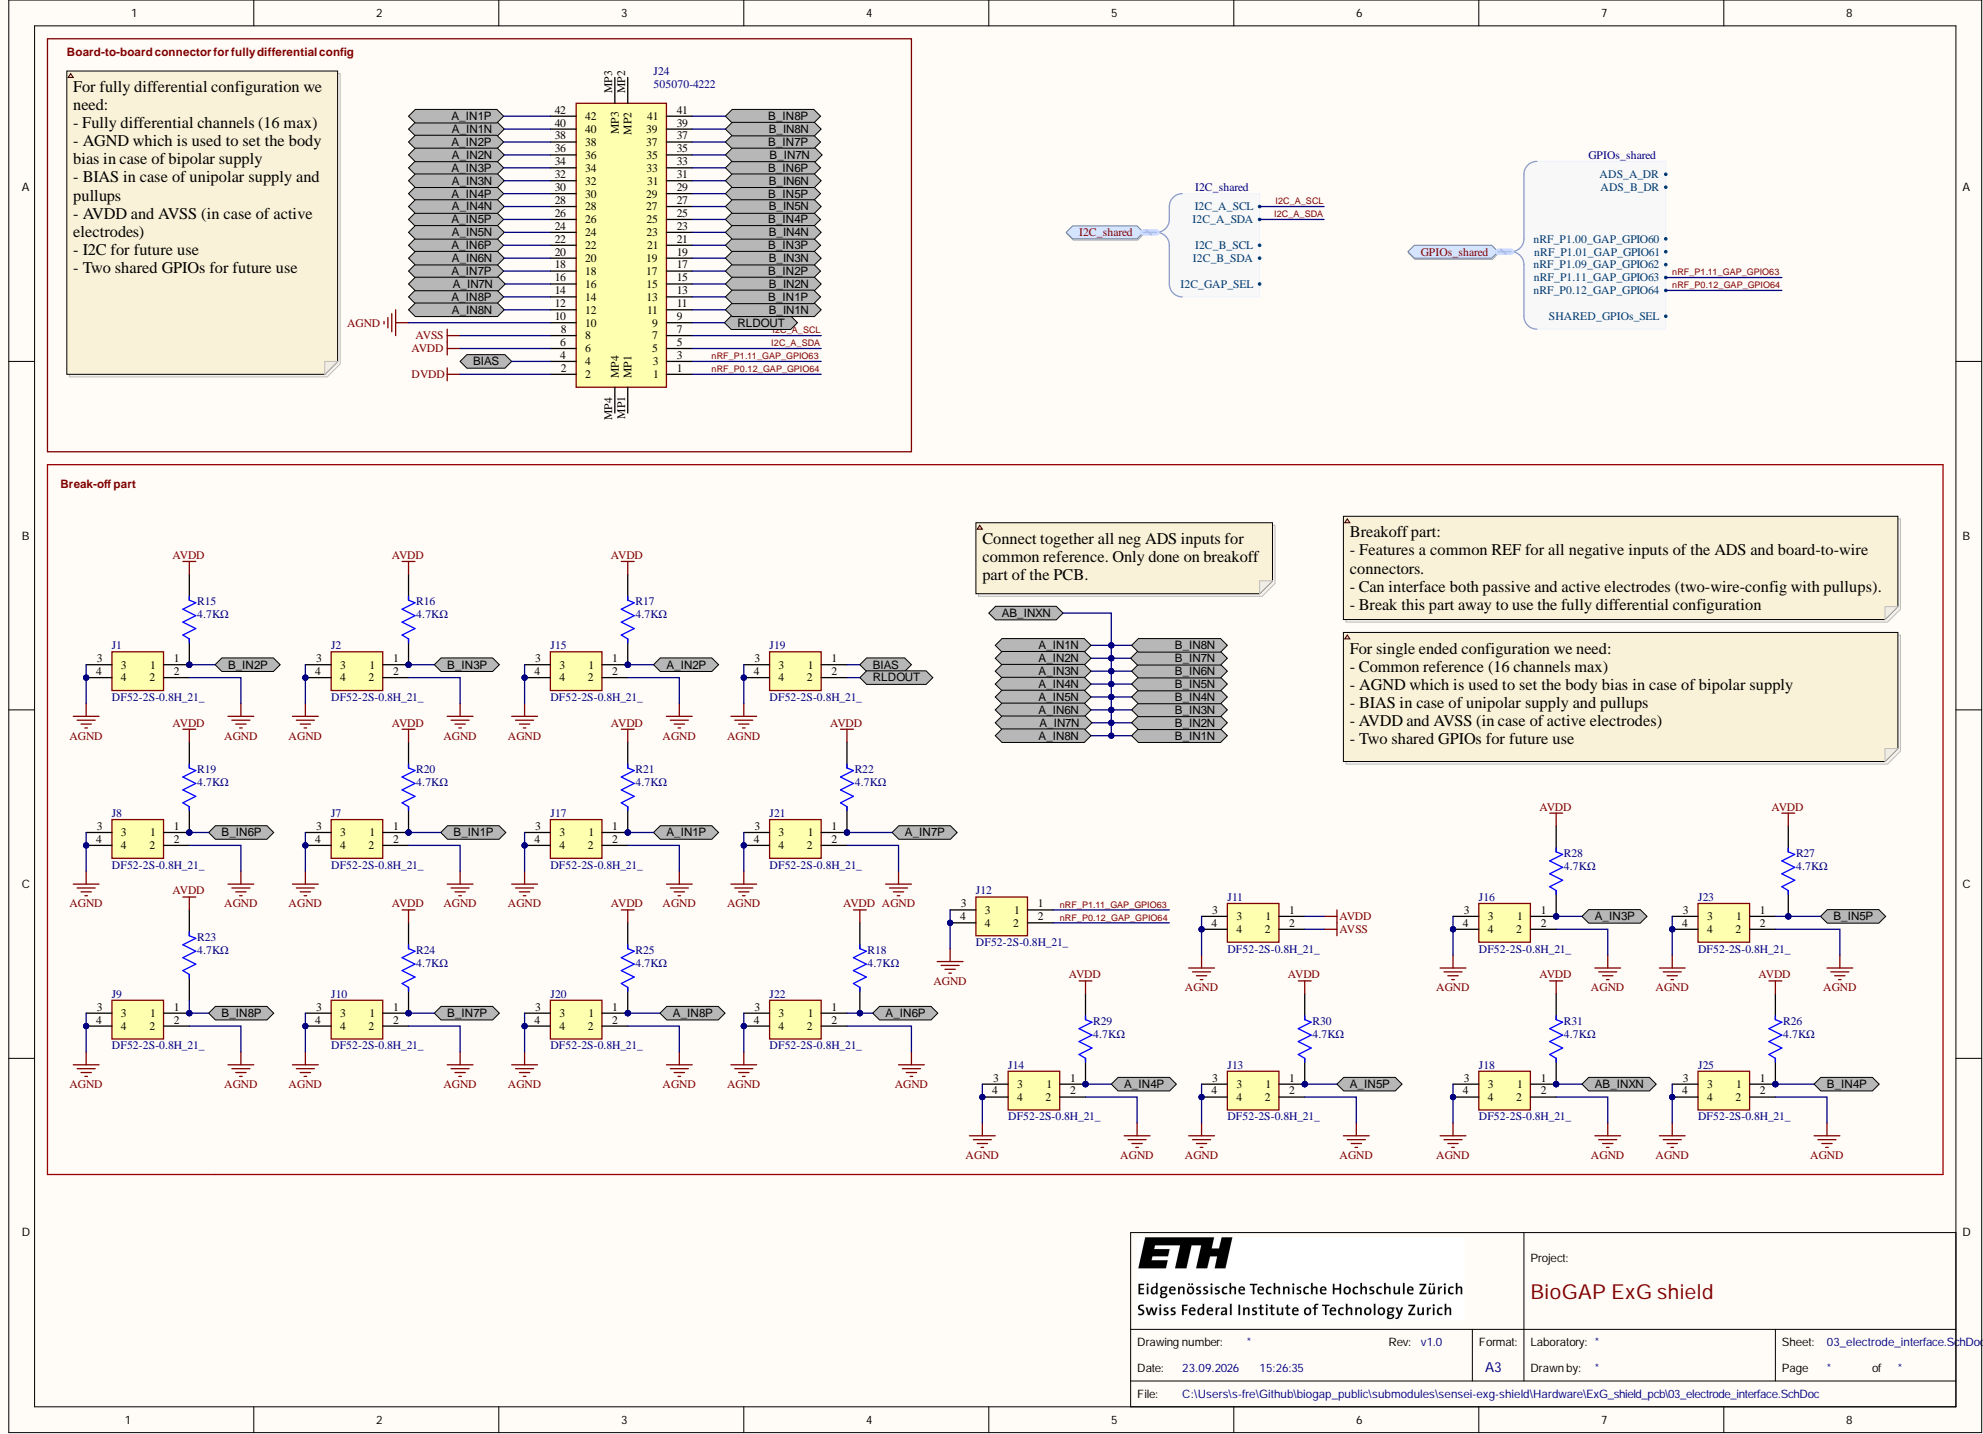
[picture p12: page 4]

Board-to-board connectorforfullydifferential config

For fully differential configuration we
need:
- Fully differential channels (16 max)
- AGND which is used to set the body
bias in case of bipolar supply
- BIAS in case of unipolar supply and
pullups
- AVDD and AVSS (in case of active
electrodes)
- I2C for future use
- Two shared GPIOs for future use

Connect together all neg ADS inputs for
common reference. Only done on breakoff
part of the PCB.

Breakoff part:
- Features a common REF for all negative inputs of the ADS and board-to-wire
connectors.
- Can interface both passive and active electrodes (two-wire-config with pullups).
- Break this part away to use the fully differential configuration

For single ended configuration we need:
- Common reference (16 channels max)
- AGND which is used to set the body bias in case of bipolar supply
- BIAS in case of unipolar supply and pullups
- AVDD and AVSS (in case of active electrodes)

Project: BioGAP ExG shield

Drawing number: * | | Laboratory: * * | Page * of *

C:\Users\s-fre\Github\biogap_public\submodules\sensei-exg-shield\Hardware\ExG_shield_pcb\03_electrode_interface.SchDoc
